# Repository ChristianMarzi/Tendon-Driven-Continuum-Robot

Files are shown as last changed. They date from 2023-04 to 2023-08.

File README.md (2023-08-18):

# Antagonistic Tendon Driven Continuum Robot
***A continuum robot for research with 4 DOF and tendon force measurement.***

robot_image

# Contents 
In this repository you will find all necessary step files to build your own continuum robot. It drives 2 tendons with a single servo to provide a simple and cost efficient setup for continuum robot research. The tendons are routed via load cells to provide tendon force measurement. The focus of this repository is the mechanical setup but basic interfacing software/information to the Robot Operating System (ROS) is provided. All 3D-printed parts are designed for SLS printing. The files are created using Autodesk Inventor 2022, for versatility step files are provided. Software and information to interface the robot to (ROS) is provided.  

## Robot System
The robot consists of 4 modules
* **Substruction**: Containing power supply, Arduino and Measurement Hardware for the load cells.
* **Base**: Base plate with mount for robot, servos and tendon pulleys.
* **Force Measurement**	: Mounts for load cells. Pulleys mounted on load cells and tensioning mechanism
* **Robot Body**: The actual robot, consisting of Nitinol backbone and spacer disks.

Off-the-shelf parts are the following:
* **Servo Motors:** [SunFounder SF3218MG](https://www.sunfounder.com/products/20kg-high-torque-servo)
* **Load Cells:** [5kg TAL220B](https://www.sparkfun.com/products/14729)
* **Tendons:** Shimano BeastMaster AX Round Dyneema
* **Bearings:** 683ZZ ball bearings 3 mm x 7 mm x 3 mm
* **Arduino Uno**
* **Various Blots and Nuts** 

## Software

### Arduino / Servo Control
The Arduino uses [rosserial](http://wiki.ros.org/rosserial) to provide topics to the ROS-network. The firmware is found in `firmware/motor_driver/motor_driver.ino`. The robot subscribes to a topic for each motor and sets the motor position with every newly arriving message. For help on setting up the [Arduino](https://www.arduino.cc/en/Guide/Introduction) refer to the Arduino and [rosserial](http://wiki.ros.org/rosserial_arduino/Tutorials/Arduino%20IDE%20Setup) documentation. 

### Load Cells
For digitizing the load cell values [Phidget 4-Input Bridges](https://www.phidgets.com/?tier=3&catid=98&pcid=78&prodid=1027) are used. A suitable ROS package is provided [here](http://wiki.ros.org/phidgets_drivers). It publishes the values to individual topics.

# Setup
As a reference, the whole System is provided as step file in full_robot.stp. It includes screws and bought parts. The `Modules_and_BOM.pdf` provides some info on assembly and required materials.   

# Paper
The paper describing the presented robot is published [here](https://www.degruyter.com/document/doi/10.1515/auto-2023-0066/html). When using this work please cite: 
Marzi, Christian, Buck, Felix and Mathis-Ullrich, Franziska. *"Continuum robot actuation by a single motor per antagonistic tendon pair: workspace and repeatability analysis"* at - Automatisierungstechnik, vol. 71, no. 7, 2023, pp. 528-536. https://doi.org/10.1515/auto-2023-0066

# Authors
Contributers of this work are
* Felix Buck
* Thomas Scherr
* [Maximilian Themistocli](https://github.com/Maxcode28)

It is maintained by Christian Marzi. The files are licensed und CERN Open Hardware Licence Version 2, see `LICENSE` for details

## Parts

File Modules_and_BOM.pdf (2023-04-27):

# Tendon Driven Continuum Robot

## Full Setup

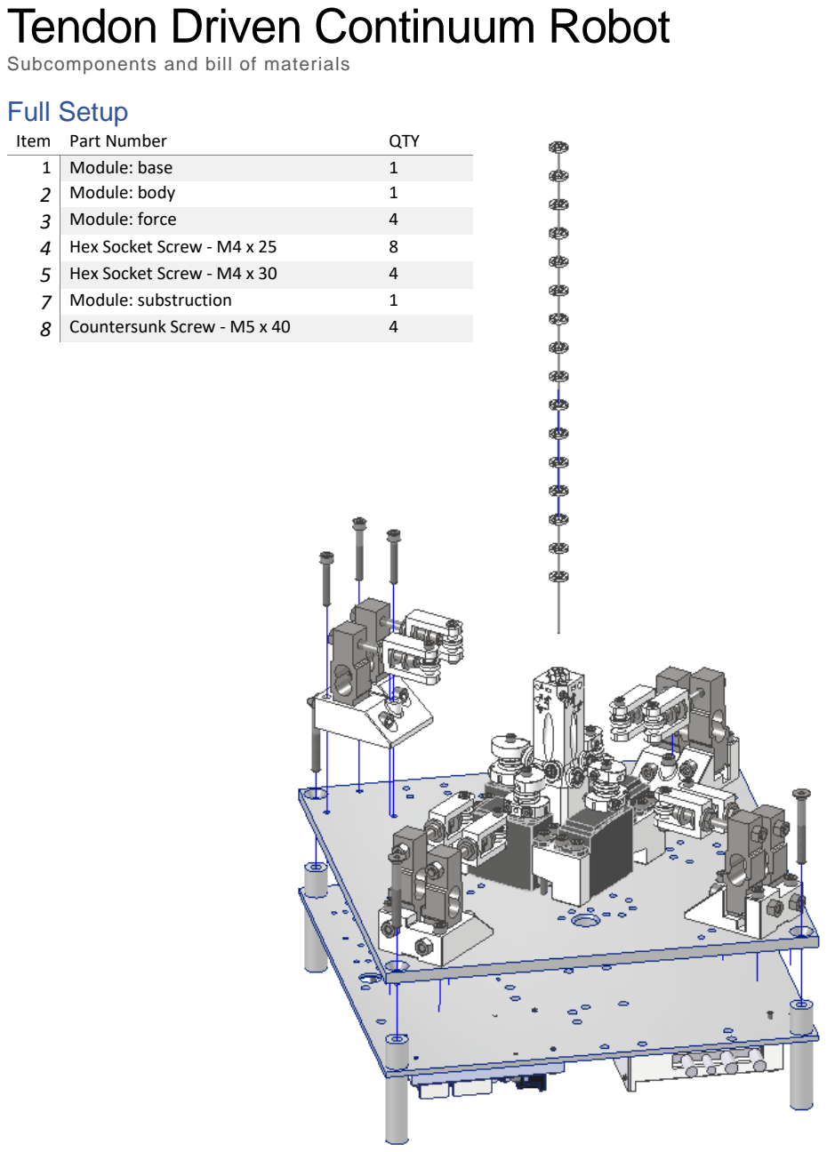
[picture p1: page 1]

Subcomponents and bill of materials

Item Part Number | QTY
1 | Module: base | 1
2 | Module: body | 1
3 | Module: force | 4
4 | Hex Socket Screw - M4 x 25 | 8
5 | Hex Socket Screw - M4 x 30 | 4
7 | Module: substruction | 1
8 | Countersunk Screw - M5 x 40 | 4

## Base

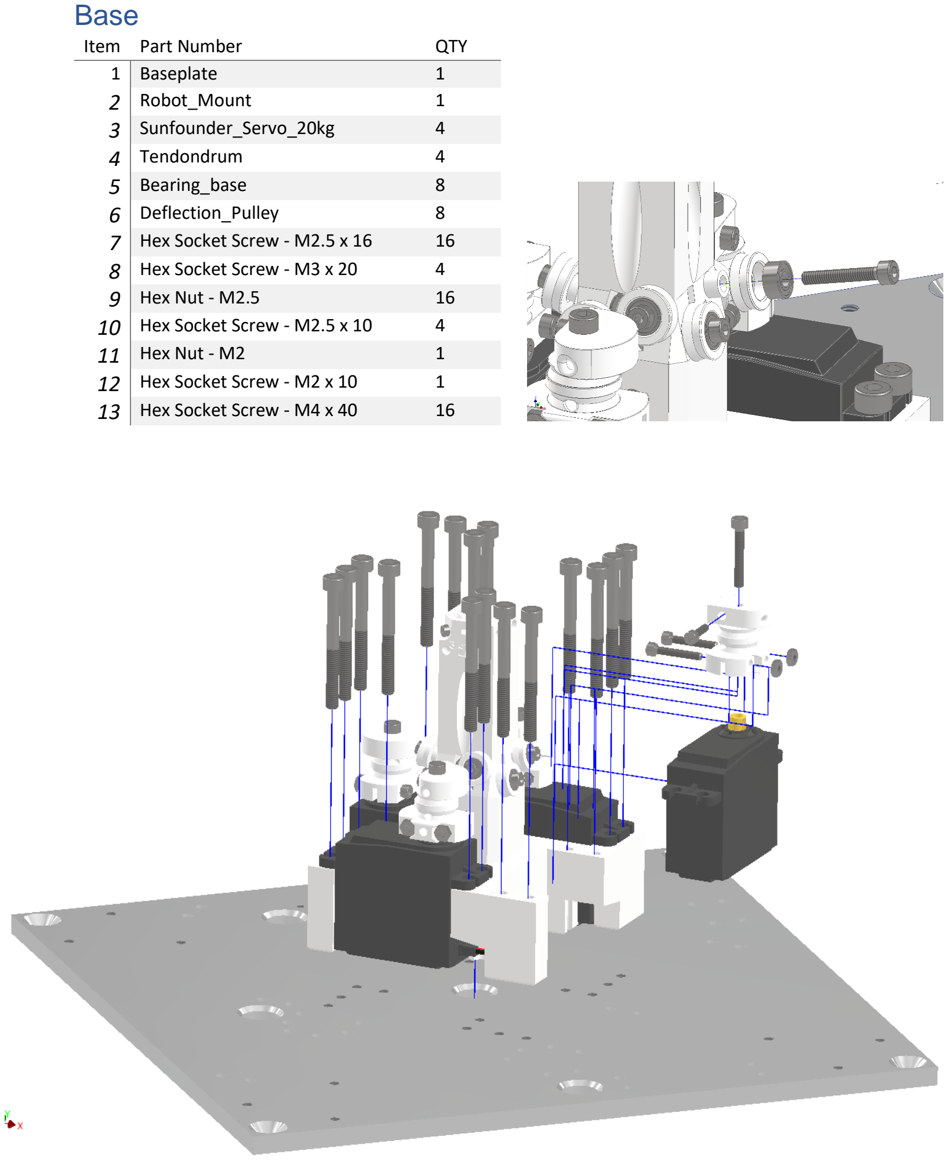
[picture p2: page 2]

Item Part Number | QTY
1 | Baseplate | 1
2 | Robot_Mount | 1
3 | Sunfounder_Servo_20kg | 4
4 | Tendondrum | 4
5 | Bearing_base | 8
6 | Deflection_Pulley | 8
7 | Hex Socket Screw - M2.5 x 16 | 16
8 | Hex Socket Screw - M3 x 20 | 4
9 | Hex Nut - M2.5 | 16
10 | Hex Socket Screw - M2.5 x 10 | 4
11 | Hex Nut - M2 | 1
12 | Hex Socket Screw - M2 x 10 | 1
13 | Hex Socket Screw - M4 x 40 | 16

## Force Unit

Item Part Number | QTY
1 | LoadCell_mount | 1
2 | Loadcell_pulley | 2
3 | LoadCell_5kg | 2
4 | Pulley_Holder_V2 | 2
5 | Pulley_Spacer_Bottom | 2
6 | Pulley_Spacer_Top | 2
7 | Bearing | 2
8 | BS EN ISO 4762 - M5 x 50 | 2
9 | BS EN ISO 4762 - M5 x 35 | 1
10 | BS EN ISO 4762 - M5 x 40 | 1
11 | ISO 4032 - M5 | 4
12 | AS 1237 - 6 mm | 6
13 | BS 4183 - M5 | 2
14 | BS EN ISO 4762 - M3 x 20 | 2
15 | ISO 4032 - M3 | 2

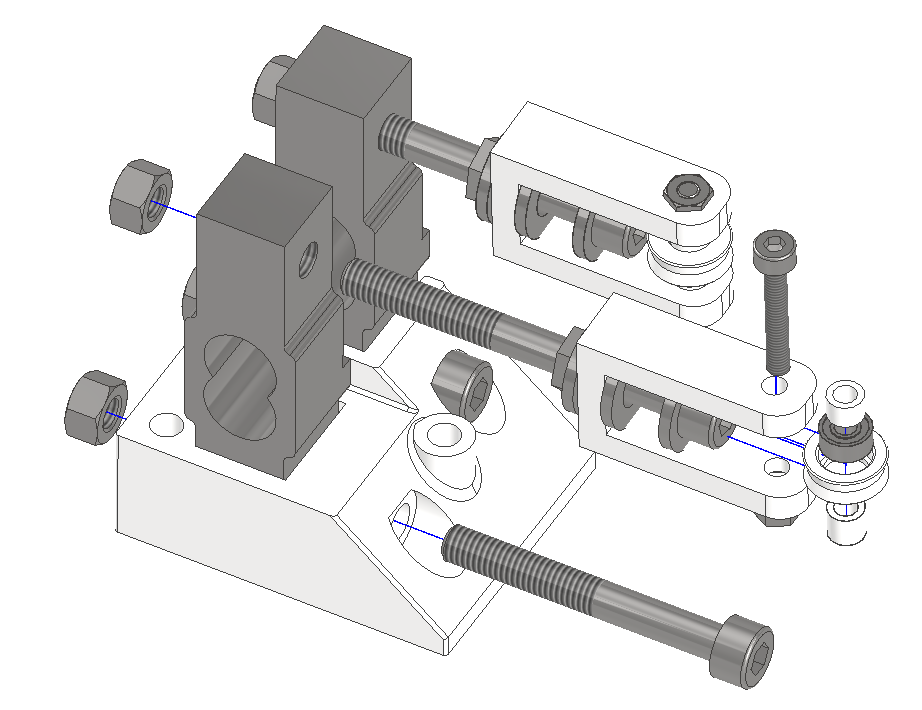
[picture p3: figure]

## Substruction

Item Part Number | QTY
1 | Substruction_mount | 1
2 | Legs | 4
3 | Spacer | 4
4 | Arduino | 1
5 | PhidgetBridge | 2
6 | PhidgetBridge_Spacer | 1
7 | PhidgetBridge_Spacer_low | 1
8 | Powersupply | 1
9 | Powersupply_cover | 1
10 | Hex Socket Screw - M2.5 x 12 | 2
11 | Hex Socket Screw - M3 x 12 | 2
12 | Hex Socket Screw - M3 x 5 | 1
13 | Hex Socket Screw - M3 x 30 | 1
14 | Hex Socket Screw - M2.5 x 16 | 1

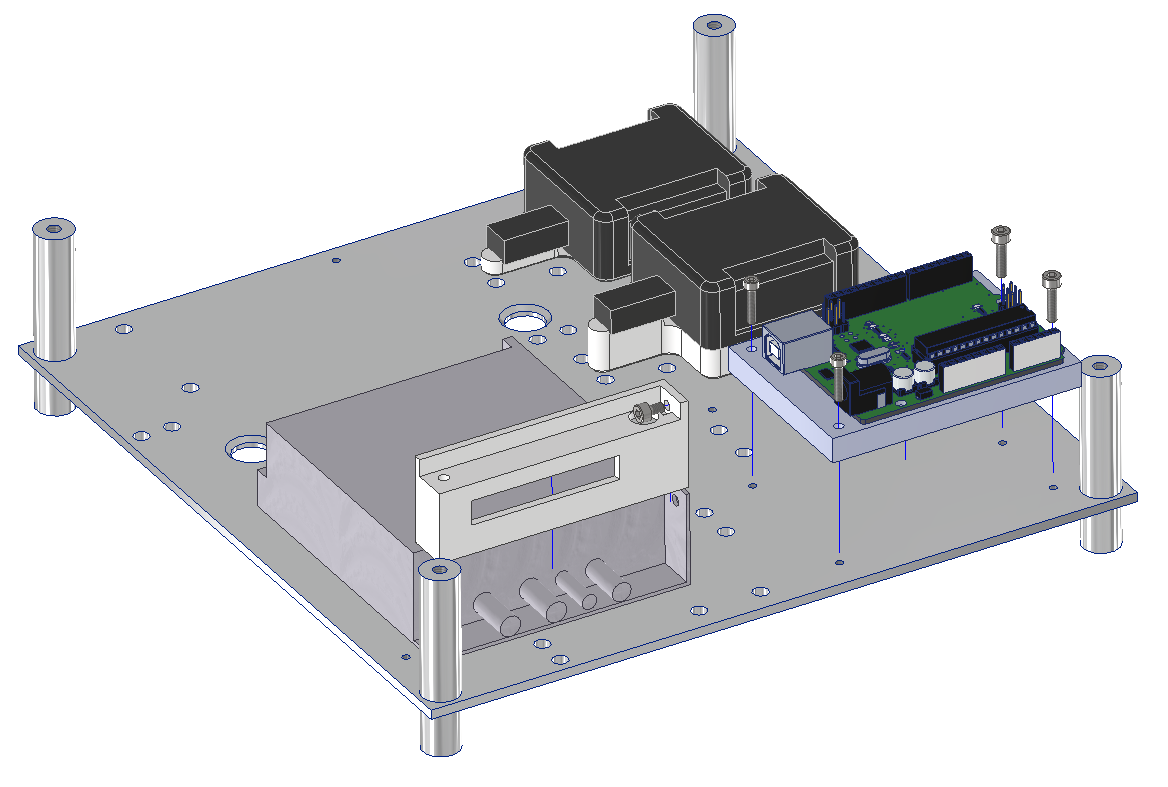
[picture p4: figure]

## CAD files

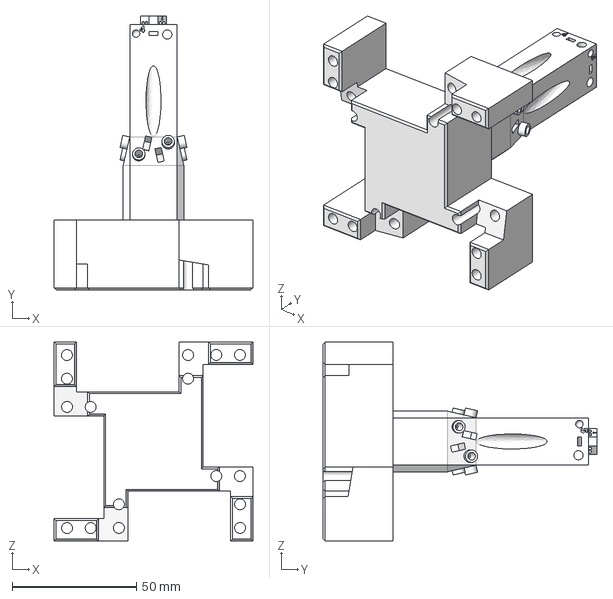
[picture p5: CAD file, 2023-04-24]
base/Robot_mount.stp
80.0 x 110.0 x 80.0 mm

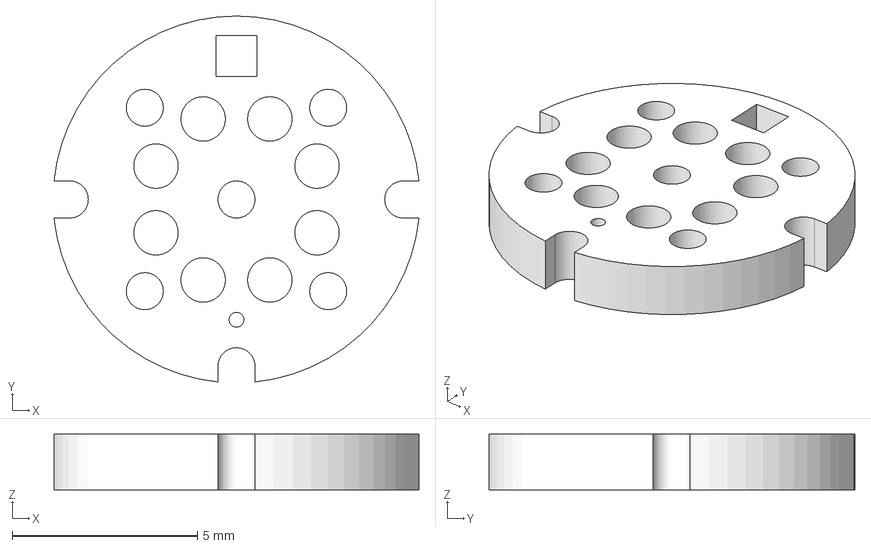
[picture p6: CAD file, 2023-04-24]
body/Spacer.stp
9.85 x 9.87 x 1.50 mm

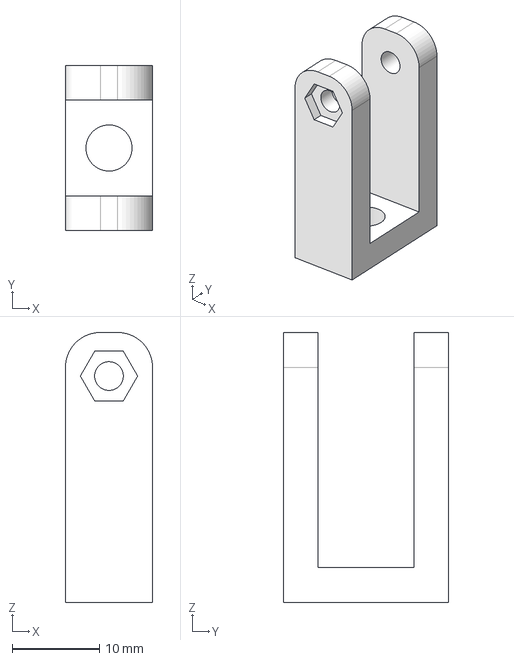
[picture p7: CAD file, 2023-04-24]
force/Pulley_mount.stp
10.0 x 19.0 x 31.0 mm

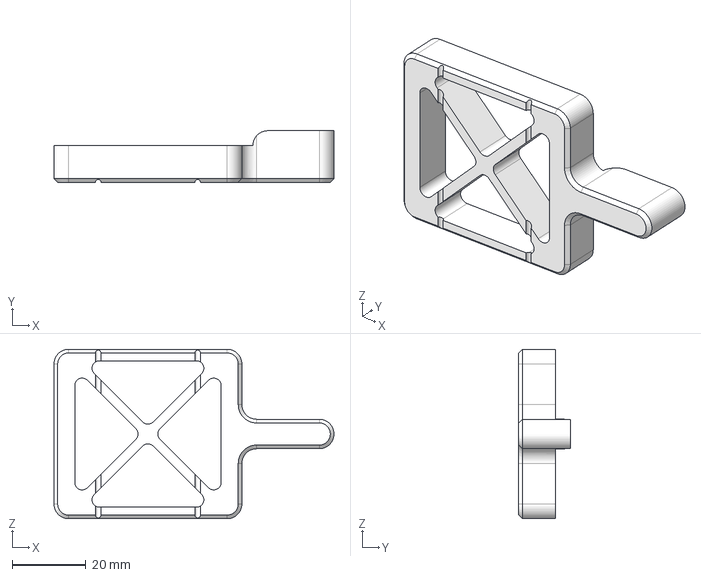
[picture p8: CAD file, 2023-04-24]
substruction/PhidgetBridge_Spacer.stp
76.0 x 14.0 x 46.0 mm

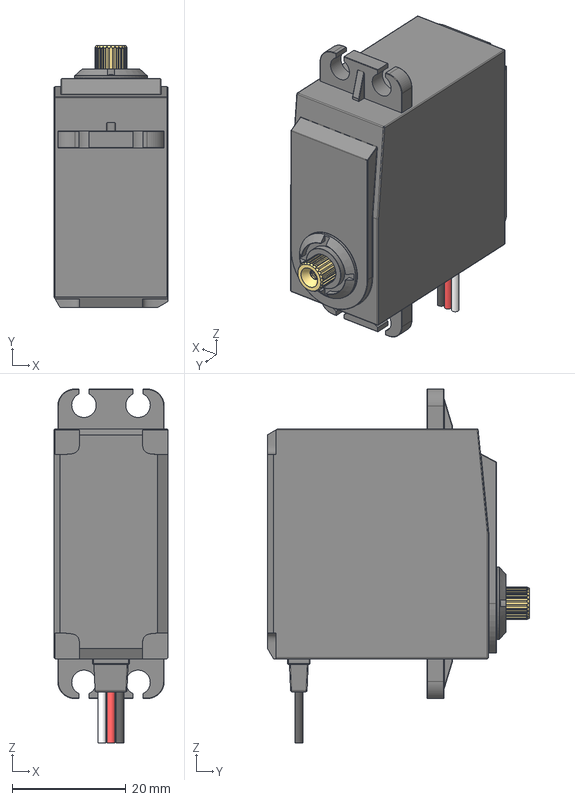
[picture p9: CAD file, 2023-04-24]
base/Servo.stp
20.0 x 46.0 x 62.2 mm

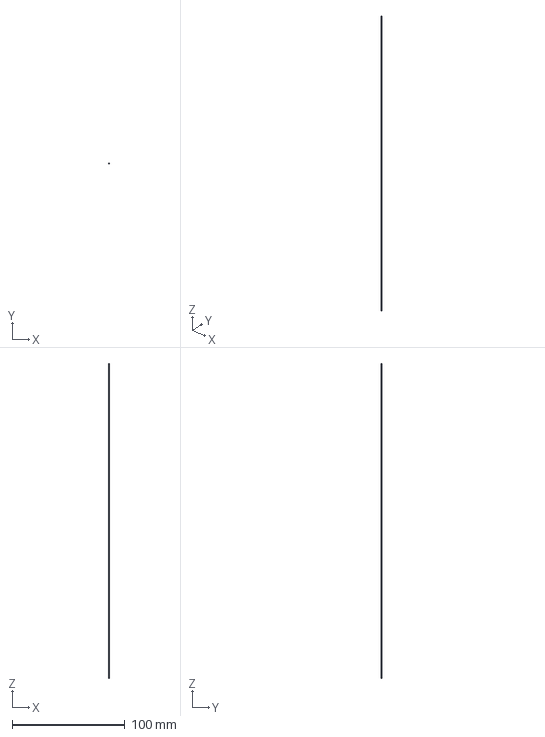
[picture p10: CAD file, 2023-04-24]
body/Backbone.stp
0.999 x 1 x 280.0 mm

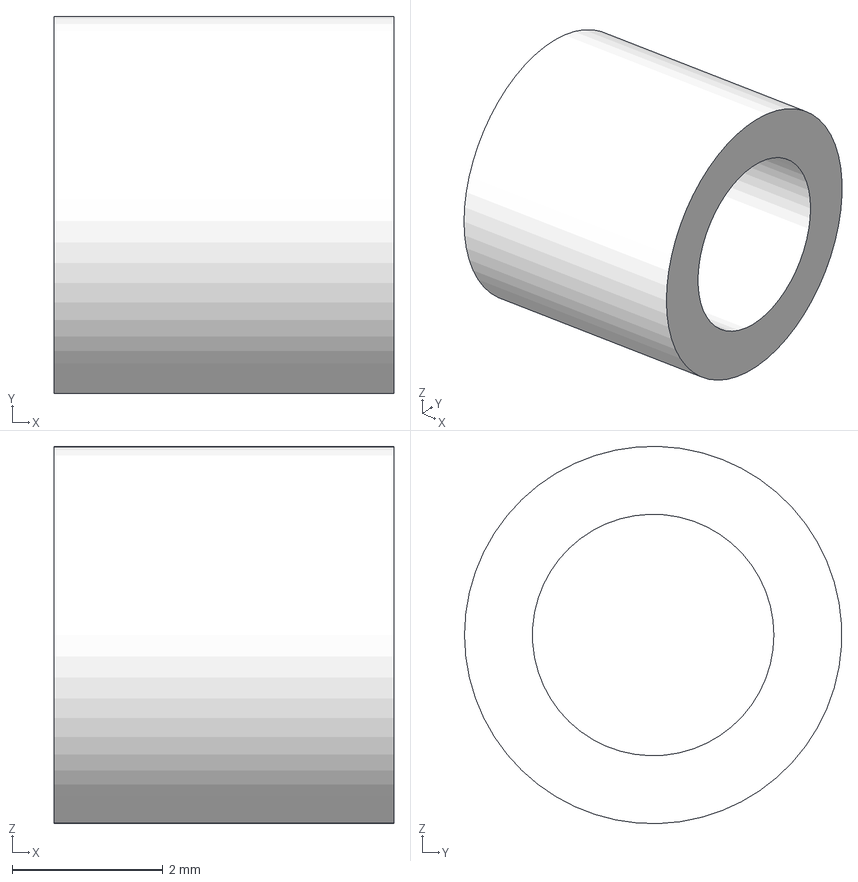
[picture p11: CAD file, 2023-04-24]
force/Pulley_spacer_top.stp
4.50 x 5.00 x 5.00 mm

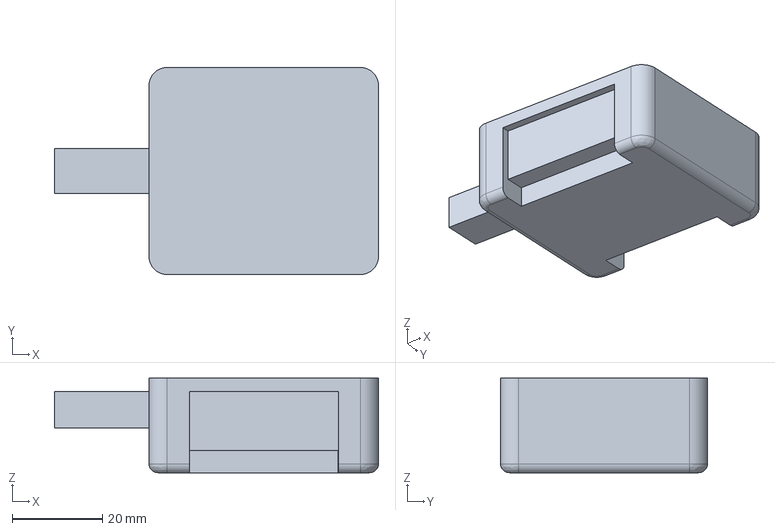
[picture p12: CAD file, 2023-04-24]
substruction/PhidgetBridge.stp
72.0 x 46.0 x 21.0 mm

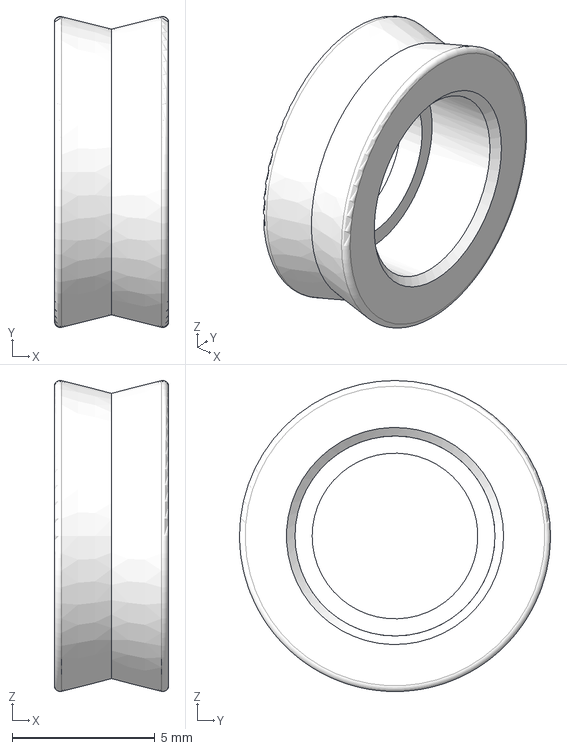
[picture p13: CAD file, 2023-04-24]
base/Deflection_pulley.stp
4.00 x 10.9 x 10.9 mm

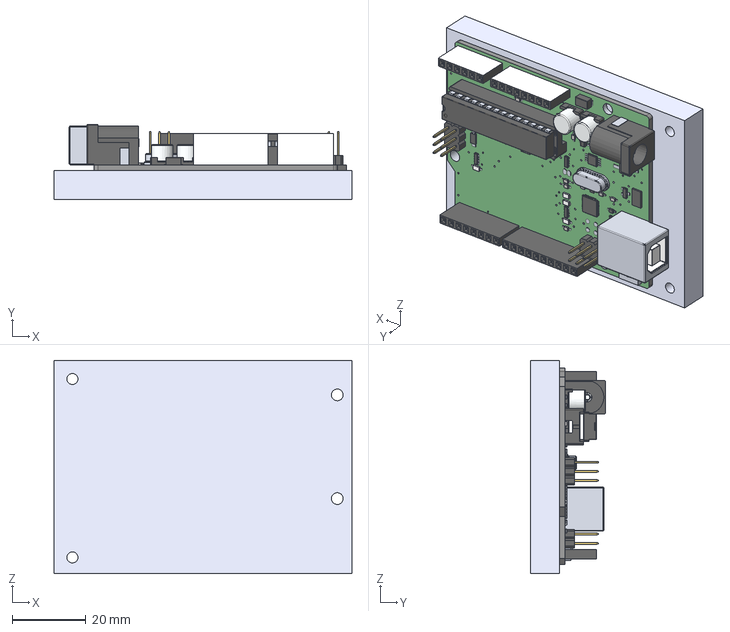
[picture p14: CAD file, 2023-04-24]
substruction/Arduino.stp
81.0 x 20.5 x 58.0 mm

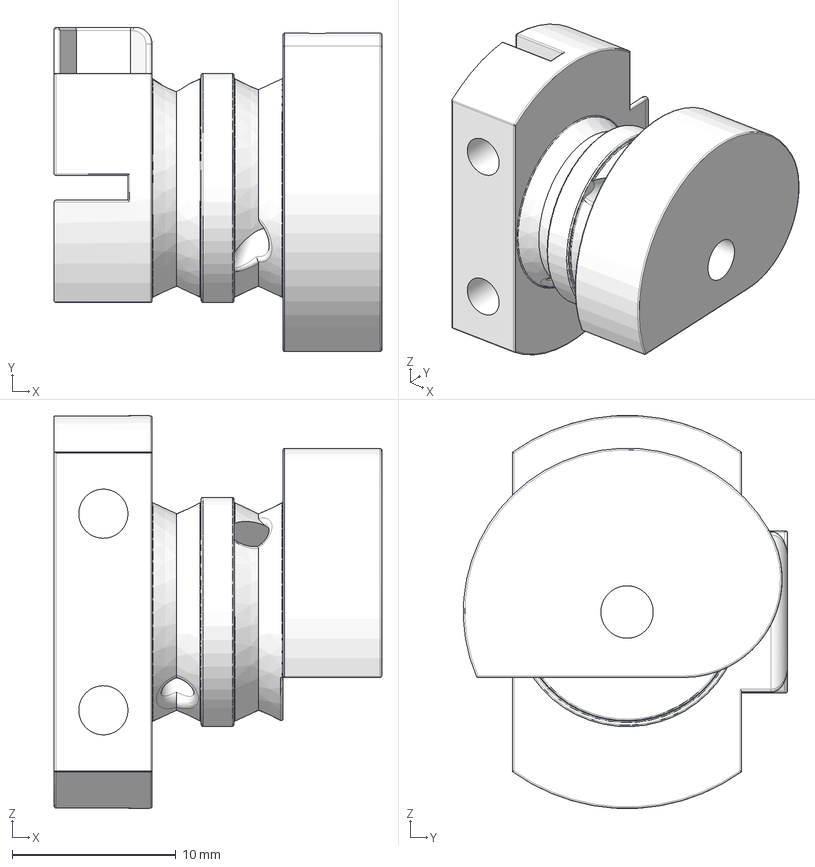
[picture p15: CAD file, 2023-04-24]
base/Tendondrum.stp
20.0 x 19.8 x 24.0 mm

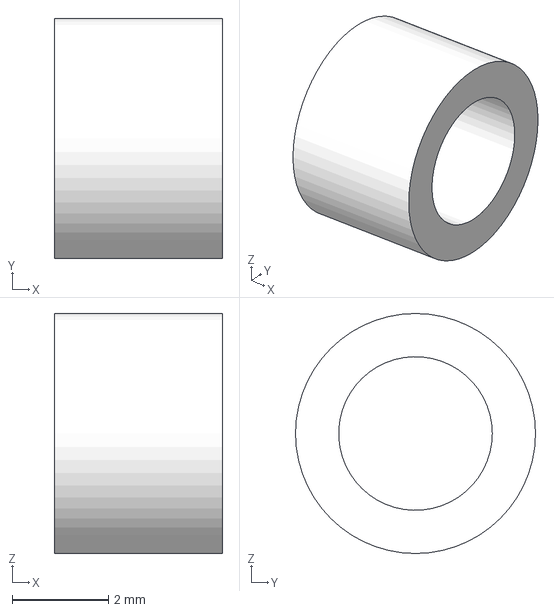
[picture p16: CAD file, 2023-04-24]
force/Pulley_spacer_bottom.stp
3.50 x 5.00 x 5.00 mm

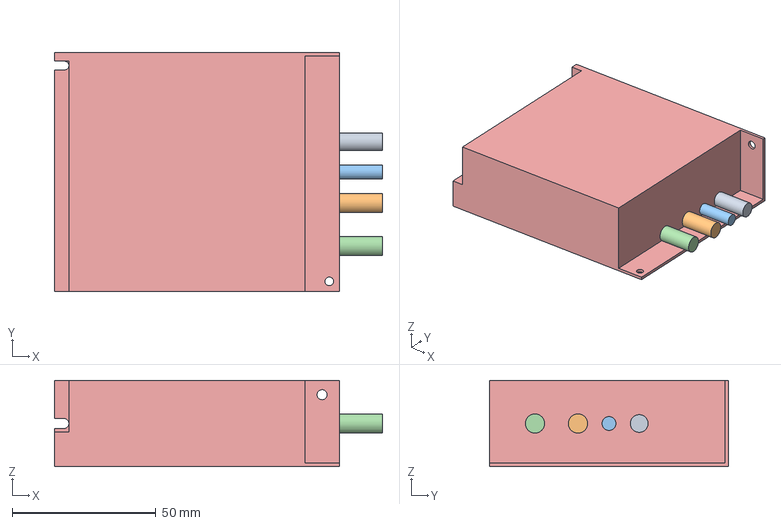
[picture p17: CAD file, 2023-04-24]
substruction/Powersupply.stp
114.0 x 83.0 x 30.0 mm

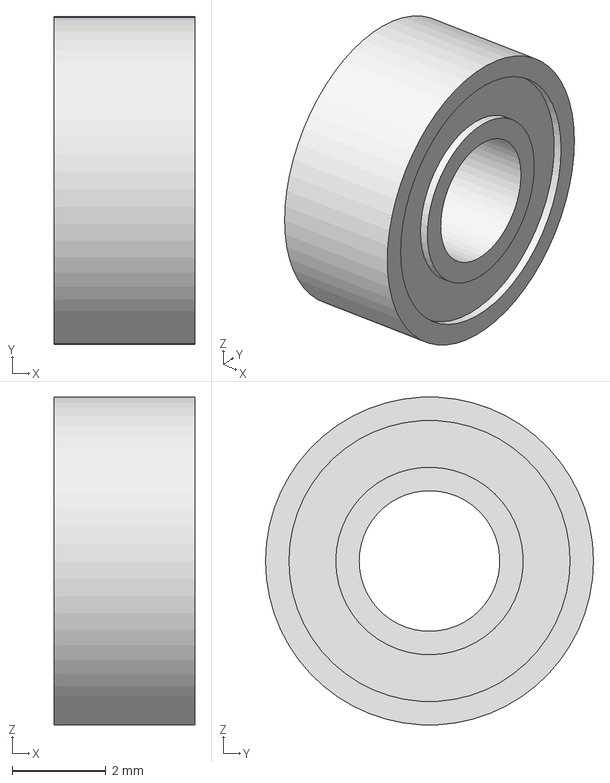
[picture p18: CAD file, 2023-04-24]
base/Bearing.stp
3.00 x 7.00 x 6.99 mm

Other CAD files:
force/Loadcell_pulley.stp
force/Loadcell_mount.stp
substruction/Substruction_mount.stp
base/Baseplate.stp
force/Loadcell.stp
substruction/Legs.stp
substruction/PhidgetBridge_Spacer_low.stp
substruction/Powersupply_cover.stp
substruction/Spacer.stp

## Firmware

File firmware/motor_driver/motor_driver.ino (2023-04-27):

#include <Servo.h> 
#include <ros.h>
#include <std_msgs/UInt16.h>

ros::NodeHandle  nh;

Servo servo_section1_x;
Servo servo_section1_y;
Servo servo_section2_x;
Servo servo_section2_y;

void servox_sec1_cb( const std_msgs::UInt16& cmd_msg){
  servo_section1_x.writeMicroseconds(cmd_msg.data); 
}

void servoy_sec1_cb( const std_msgs::UInt16& cmd_msg){
  servo_section1_y.writeMicroseconds(cmd_msg.data); 
}

void servox_sec2_cb( const std_msgs::UInt16& cmd_msg){
  servo_section2_x.writeMicroseconds(cmd_msg.data); 
}

void servoy_sec2_cb( const std_msgs::UInt16& cmd_msg){
  servo_section2_y.writeMicroseconds(cmd_msg.data); 
}

ros::Subscriber<std_msgs::UInt16> sub1("Servox_sec1_us", servox_sec1_cb);
ros::Subscriber<std_msgs::UInt16> sub2("Servoy_sec1_us", servoy_sec1_cb);
ros::Subscriber<std_msgs::UInt16> sub3("Servox_sec2_us", servox_sec2_cb);
ros::Subscriber<std_msgs::UInt16> sub4("Servoy_sec2_us", servoy_sec2_cb);

void setup(){
  nh.initNode();
  nh.subscribe(sub1);
  nh.subscribe(sub2);
  nh.subscribe(sub3);
  nh.subscribe(sub4);
  
  servo_section1_x.attach(3); //attach it to pin 3
  servo_section1_y.attach(5); //attach it to pin 5
  servo_section2_x.attach(6); //attach it to pin 6
  servo_section2_y.attach(9); //attach it to pin 9
}

void loop(){
  nh.spinOnce();
  delay(1);
}

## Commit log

2023-04-27 Added Arduino firmware
2023-04-27 added assembly doc
